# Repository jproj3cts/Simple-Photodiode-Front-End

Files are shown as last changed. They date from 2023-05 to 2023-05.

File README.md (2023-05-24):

# Simple-Photodiode-Front-End (Work in progress)
This project aims to provide a simple slow (~15KHz) but very cheap and low noise large area photodiode front end, for the use in building scientific instrumentation.

## BILL OF MATERIALS
  ```
PBSS4360PA5-QX
TC1014-3.3VCT713
OPT101P-J
0805 Resistors
0805 Ceramic Capacitors
0805 Tantalum Capacitor (optional)
  ```
 ## Circuit Design

The general scheme of this device is shown below. As can be seen, it is formed of three sections: a capacitance multiplier, a 3.3V regulator, and the OPT101 itself. The first two stages function to minimise input noise as much as possible, with the capacitance multiplier functioning to almost entirely remove mains ripple. The OPT101 is a monolithic photodiode and single-supply transimpedance amplifier, so conveniently amplifies the photodiode output without requiring an external TIA and biases the device too. The disadvantage of course is that it has a relatively limited bandwidth of ~15KHz, but this should be good enough for applications that require only a slow response time such as a spectrophotometer.

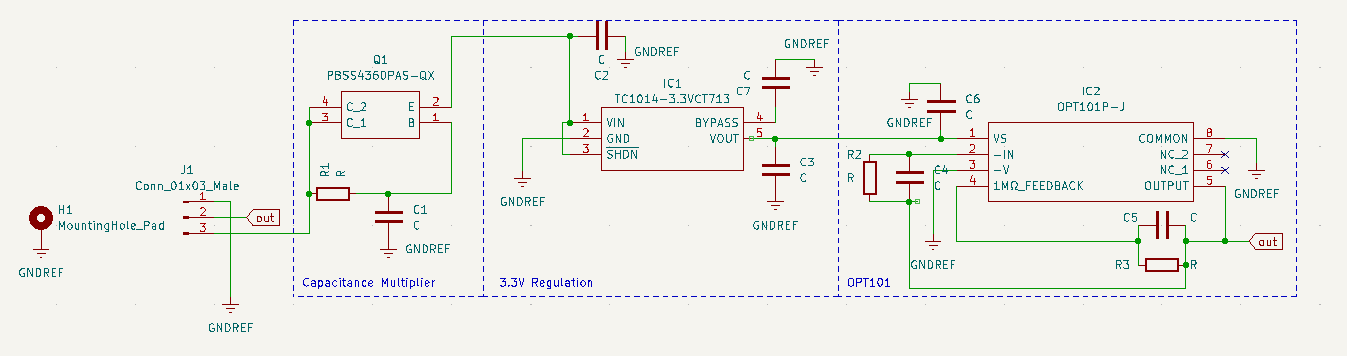
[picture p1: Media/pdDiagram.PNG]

  
 ## Assembly

The PCB itself can be fabricated using your favorite online service by simply uploading the "photodiode for fabrication.zip" file to their online store. I go with JLCPCB, but others are available. Assebly should also be possible using these services if you provide a BOM too, though some special considerations may need to be made for the OPT101 chip since it is an optical component. Elsewise, you can do what I did and hand solder the components.

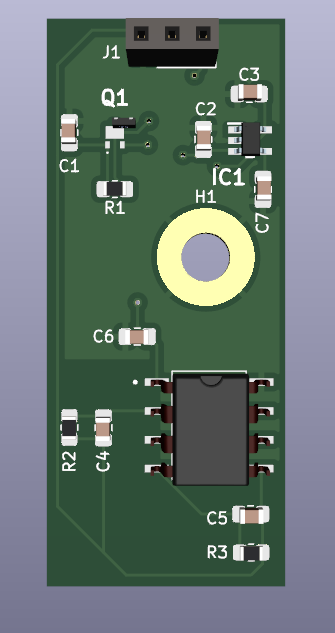
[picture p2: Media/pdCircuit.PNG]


It is an option to use a tantalum capacitor for C1 to avoid the microphonics associated with ceramic ones. The device can be mounted to a case with a M4 bolt and is designed such that it has no conductive pads on its back and the area around H1 is grounded. As such, if bolted to a conductive case, the case will be grounded and act as an EMI shield. Using only one screw hole also allows fine angluar adjustment of the placement of the photodiode, should that be required.

R2, R3, C4, and C5 are all optional and can be used to set the gain and bandwidth of the detector yourself, details on this are in the OPT101 datasheet (https://www.ti.com/lit/ds/symlink/opt101.pdf). If you would like to use the chip with its internal gain of 1M$`\Omega`$ (0.45 A/W @ 650 nm)  then simply short R3 or C5 and leave the others empty.

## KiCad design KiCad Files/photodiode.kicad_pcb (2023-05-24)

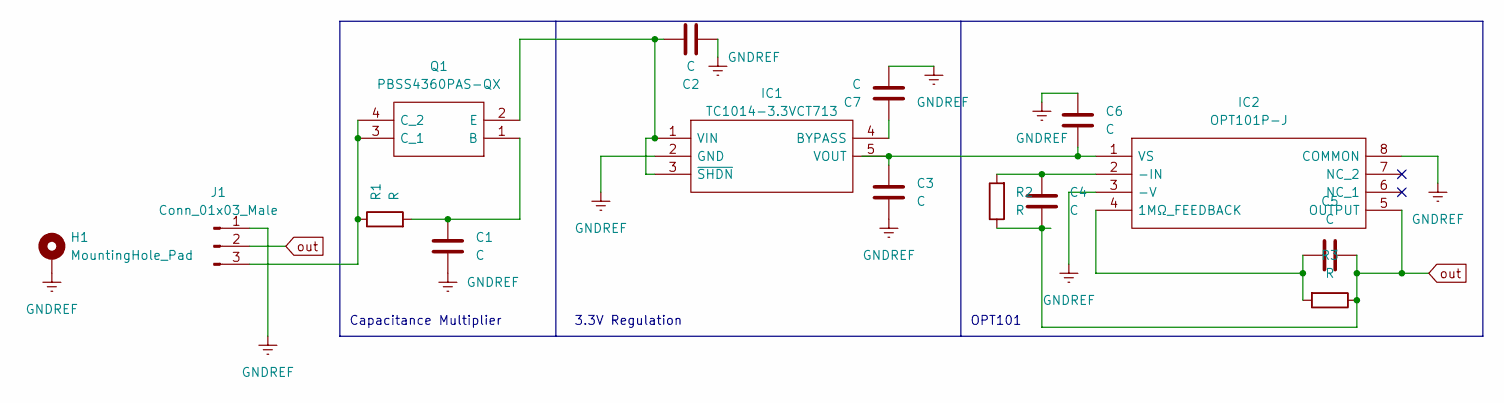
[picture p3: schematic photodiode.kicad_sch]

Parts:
C1, C2, C3, C4, C5, C6, C7: C; C_0805_2012Metric_Pad1.18x1.45mm_HandSolder
H1: MountingHole_Pad; MountingHole_4.3mm_M4_Pad
IC1: TC1014-3.3VCT713; SOT95P280X145-5N; Mouser Part Number 579-TC1014-3.3VCT713
IC2: OPT101P-J; OPT101PJ; Mouser Part Number 595-OPT101P-J
J1: Conn_01x03_Male; PinSocket_1x03_P2.54mm_Vertical
Q1: PBSS4360PAS-QX; PBSS4310PASQX; Mouser Part Number 771-PBSS4360PAS-QX
R1, R2, R3: R; R_0805_2012Metric_Pad1.20x1.40mm_HandSolder

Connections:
GNDREF: C1.1, C2.1, C3.1, C6.2, C7.1, H1.1, IC1.2 (GND), IC2.3 (-V), IC2.8 (COMMON), J1.1
unnamed: C1.2, Q1.1 (B), R1.2
unnamed: C2.2, IC1.1 (VIN), IC1.3 (~SHDN), Q1.2 (E)
unnamed: C3.2, C6.1, IC1.5 (VOUT), IC2.1 (VS)
unnamed: C4.2, IC2.2 (-IN), R2.2
unnamed: C5.2, IC2.4 (1MΩ_FEEDBACK), R3.2
unnamed: C7.2, IC1.4 (BYPASS)
unnamed: J1.3, Q1.3 (C_1), Q1.4 (C_2), R1.1
out: C4.1, C5.1, IC2.5 (OUTPUT), J1.2, R2.1, R3.1

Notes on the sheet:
3.3V Regulation
OPT101
Capacitance Multiplier

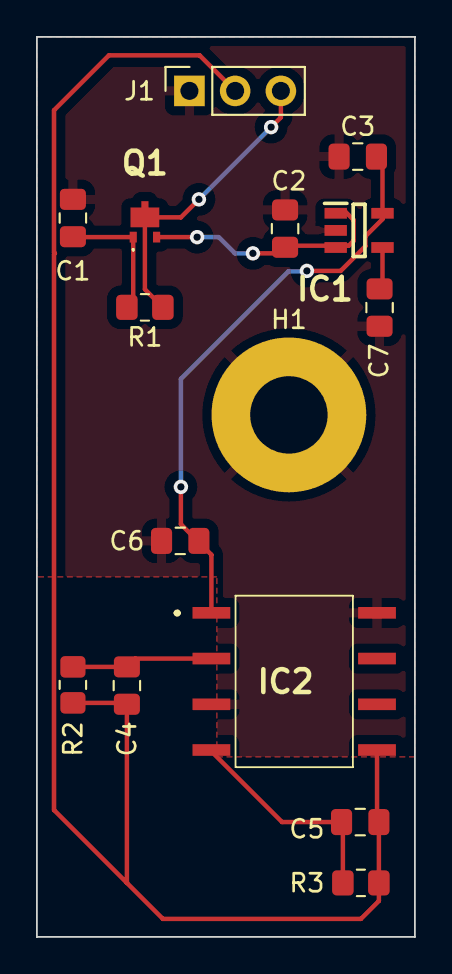
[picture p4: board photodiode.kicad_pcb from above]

Board: 2 copper layers, 21.0 x 50.0 mm, 15 parts (0 on the bottom side), 9 nets.
